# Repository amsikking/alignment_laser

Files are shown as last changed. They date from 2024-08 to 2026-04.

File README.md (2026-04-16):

# alignment_laser



How to build a simple alignment laser for typical optical alignment tasks.

## Overview:
This alignment laser is fast and simple to build, and easy to move around the lab. It can be used for most alignment tasks, from simple arrangements (e.g. placing a few mirrors) to complex systems (e.g. building sophisticated microscopes).

**Note:** It is not essential to copy this exact design, the key features and methods shown here can be applied to other setups.

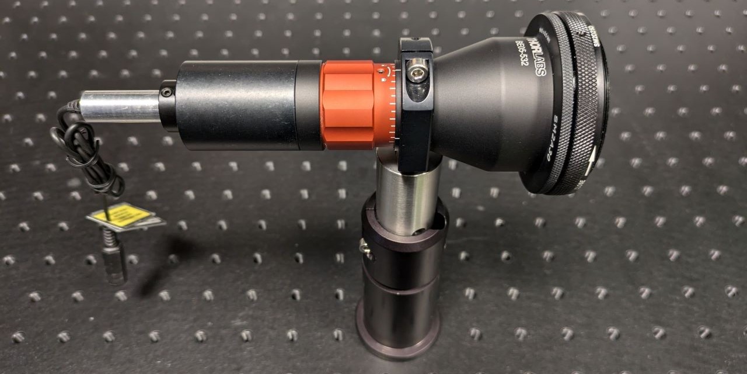
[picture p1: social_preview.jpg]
social_preview


## Features:
- **A 532nm laser diode:** this sits in the middle of the visible spectrum (~380-750nm), and is good for aligning to the central wavelength of typical achromatic lenses. Also, the human eye is sensitive to the bright green color which helps during alignment.
- **A round ~3.5mm diameter beam profile:** elliptical or otherwise asymmetric beams are difficult to work with, a round beam is usually best.
- **A power of 4.5mW:** bright enough for most tasks, but not excessive.
- **A 5x beam expander with collimation adjustment:** this gives a ~17.5mm diameter beam which is enough for most 1 inch optical alignment tasks (and exceeds most objective back focal plane diameters).
- **A variable iris:** this allows easy beam diameter adjustment in the range of ~1-17.5mm. Small diameter beams (e.g. 1mm) are good for checking back reflections and beam deviations from lenses or other optics. Large diameter beams (e.g. >5mm) are good for checking collimation and have a long propagation distance.
- **Balanced mechanics:** the assembly is easy to move around and bolt down in different positions. When paired with 2 adjustable mirrors, the alignment laser is fast to deploy in most situations.

## Build:
Go to the [cad](https://github.com/amsikking/alignment_laser/tree/main/cad) folder and open [alignment_laser_v1.0.pdf](https://github.com/amsikking/alignment_laser/blob/main/cad/alignment_laser_v1.0.PDF)
- Get the parts and screw them together (see the other CAD files for details).

## Test:
Download the repository, go to the [photos](https://github.com/amsikking/alignment_laser/tree/main/photos) folder and follow the numbered photos:

0) [**Check parts:**](https://github.com/amsikking/alignment_laser/blob/main/photos/0_all_parts_used.jpg) to follow exactly you’ll need these extra parts from Thorlabs:
    - Absorptive ND filter wheel (or filter set) for beam attenuation: NDC-100S-4M or NEK01 (or both).
    - A camera for looking at the beam profile: e.g. CS165MU1/M
    - Some shear plates for checking collimation: SI100 (5-10mm beams), SI050P (2.5-5mm beam plate) and SI254P (10-25.4mm beam plate).
    - **Note:** If you don’t have these parts, you can do something similar with other tricks (e.g. alternative beam attenuation and profiling methods, and checking collimation with distance).
1) [**Check laser collimation:**](https://github.com/amsikking/alignment_laser/blob/main/photos/1_check_laser_collimation.jpg) attenuate the beam and use the 2.5-5mm shear plate to check the laser output is collimated.
2) [**Optional -> measure beam profile:**](https://github.com/amsikking/alignment_laser/blob/main/photos/2_measure_laser_beam_profile.jpg) use a camera and compare the measured beam profile to the specification. Attenuate with ND filters on the camera and use the back reflection to align. See the [beam_profile_example](https://github.com/amsikking/alignment_laser/tree/main/beam_profile_example) folder and the [gaussian_beam_profiler](https://github.com/amsikking/gaussian_beam_profiler) repository for more.
3) [**Add target:**](https://github.com/amsikking/alignment_laser/blob/main/photos/3_align_target_to_laser.jpg) use an alignment card (or similar) and center the beam on a target.
4) [**Add 5x beam expander:**](https://github.com/amsikking/alignment_laser/blob/main/photos/4_add_collimator_and_iris.jpg) the large beam (iris open) should have a nice smooth profile over ~17.5mm.
5) [**Check beam deviation:**](https://github.com/amsikking/alignment_laser/blob/main/photos/5_close_iris_and_check_beam_deviation.jpg) with a small ~1mm beam (iris closed), check the position of the beam on the target. A small deviation of a few mm is normal after adding the beam expander since we are relying on the mechanical alignment of the parts.
6) [**Add large shear plate:**](https://github.com/amsikking/alignment_laser/blob/main/photos/6_add_large_shear_plate.jpg) With a small ~1mm beam, add the 10-25.4mm shear plate and use the double reflections to align the plate with the line on the frosted screen.
7) [**Check collimation:**](https://github.com/amsikking/alignment_laser/blob/main/photos/7_check_collimation_with_large_shear_plate.jpg) Open the iris to ~17.5mm and check the collimation with the shear plate.
8) [**Adjust collimation:**](https://github.com/amsikking/alignment_laser/blob/main/photos/8_adjust_collimation_with_large_shear_plate.jpg) use the beam expander adjuster to set the collimation with the shear plate.
9) [**Re-check collimation:**](https://github.com/amsikking/alignment_laser/blob/main/photos/9_check_collimation_with_medium_shear_plate.jpg) use the 5-10mm shear plate to double check collimation, then fix the position of the beam expander adjuster with the set screw.

If the testing goes smoothly, the portable alignment laser is now ready to use!

## Acknowledgments:
Inspired by, and with contributions from: [jlazzaridean](https://github.com/jlazzaridean), [fadero](https://github.com/fadero) and [AndrewGYork](https://github.com/AndrewGYork).

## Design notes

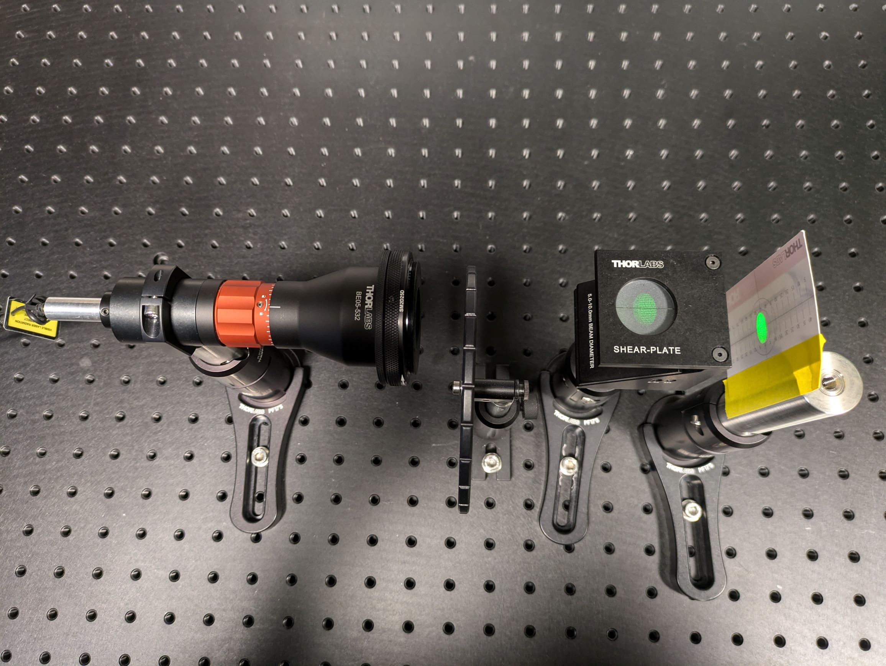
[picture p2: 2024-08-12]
photos/9_check_collimation_with_medium_shear_plate.jpg

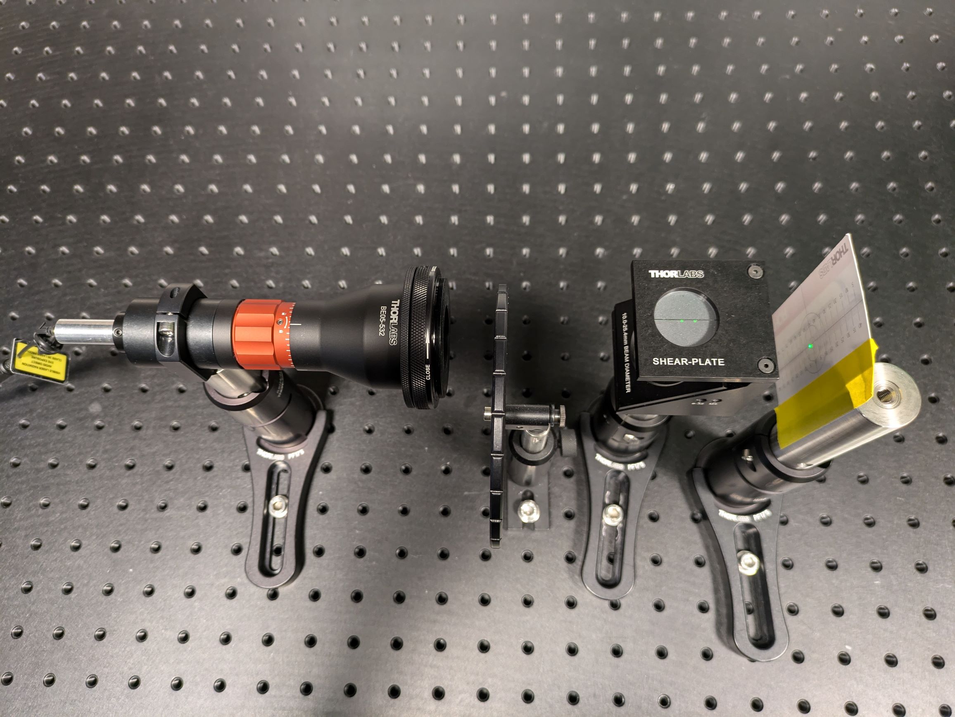
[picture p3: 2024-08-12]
photos/6_add_large_shear_plate.jpg

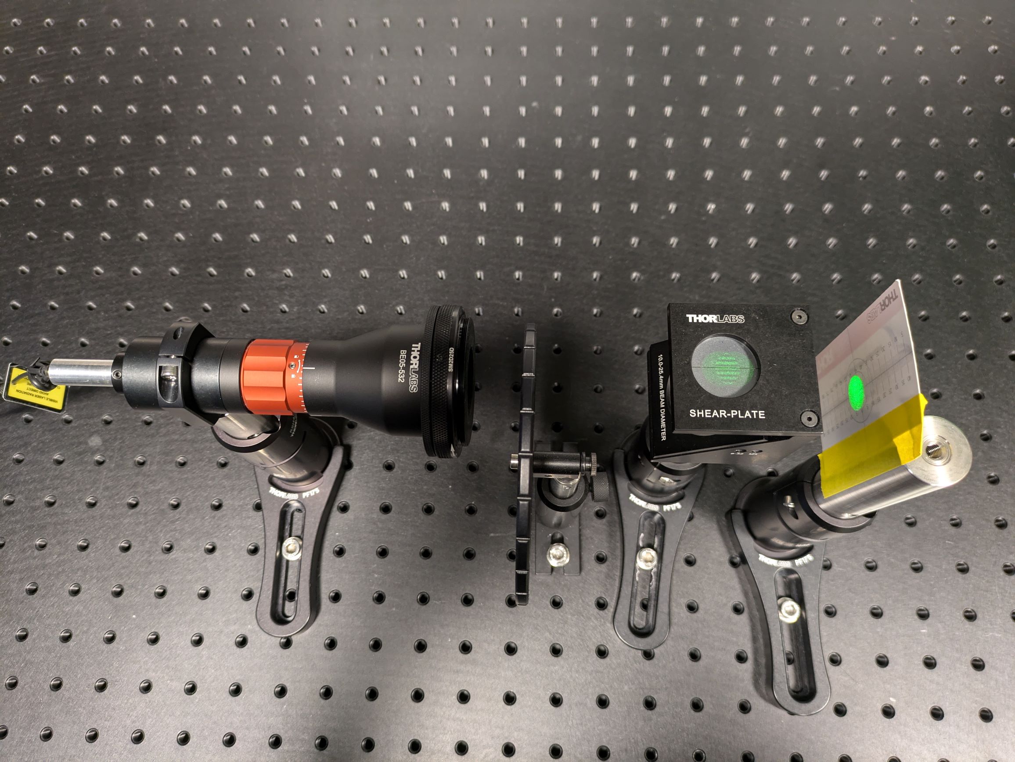
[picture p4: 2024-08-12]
photos/8_adjust_collimation_with_large_shear_plate.jpg

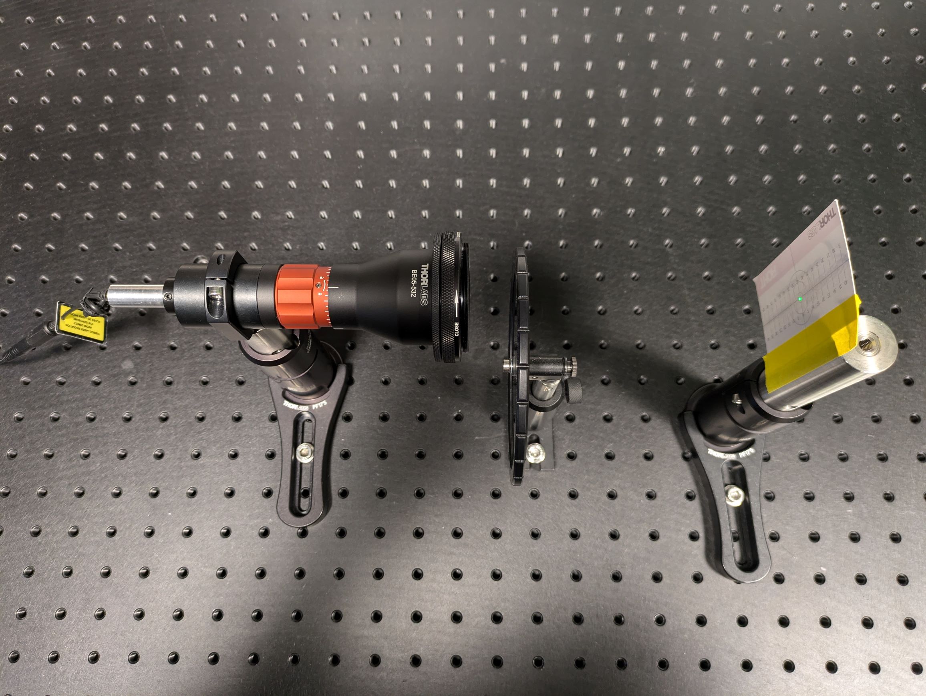
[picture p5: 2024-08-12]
photos/5_close_iris_and_check_beam_deviation.jpg

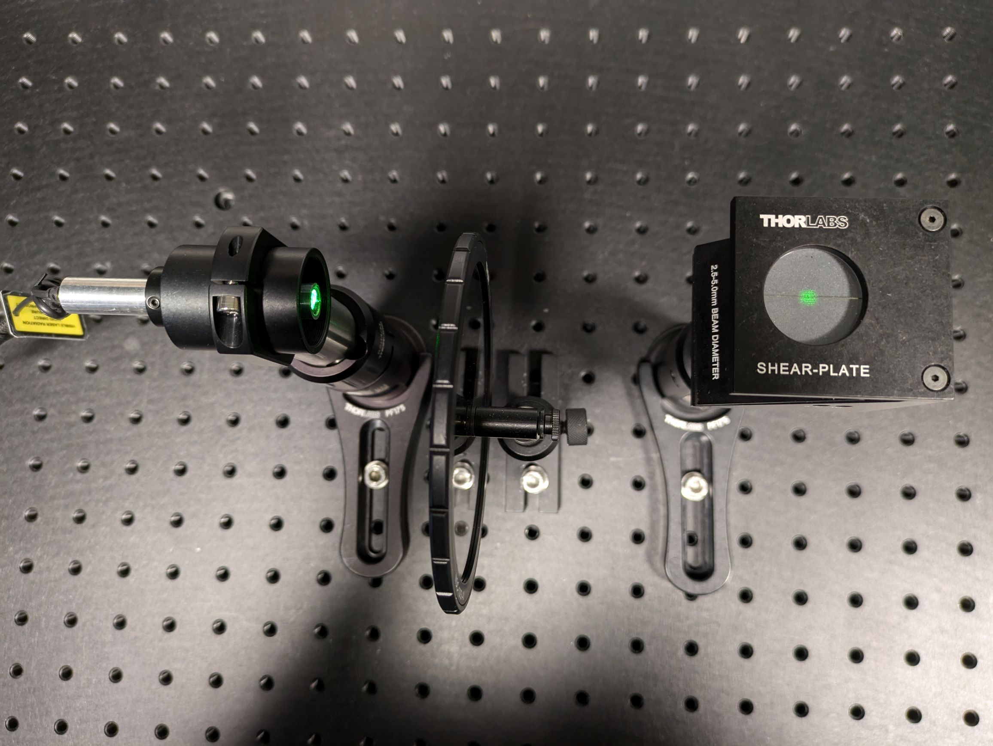
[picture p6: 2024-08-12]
photos/1_check_laser_collimation.jpg

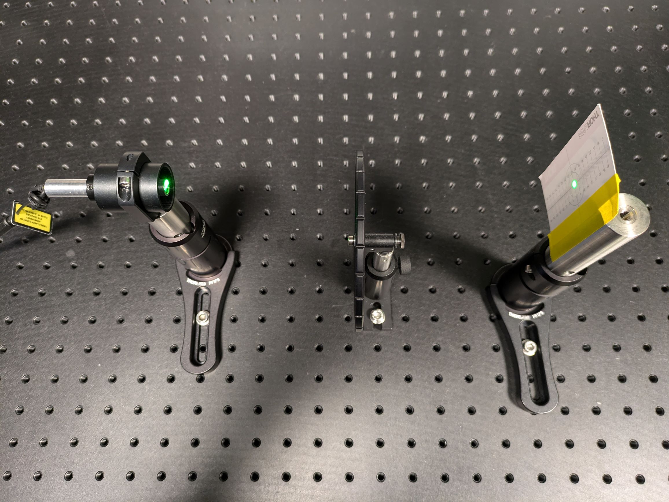
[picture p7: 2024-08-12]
photos/3_align_target_to_laser.jpg

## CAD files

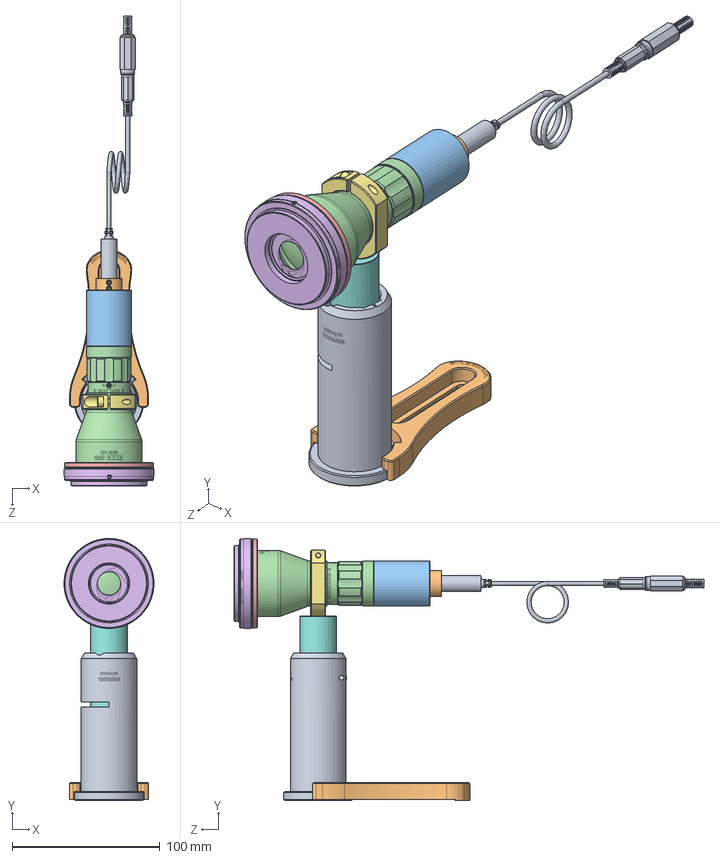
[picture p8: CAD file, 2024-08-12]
cad/alignment_laser_v1.0.SLDASM
61.0 x 177.6 x 318.3 mm
CPS532-Solidworks
AD11F-Solidworks
SM1M15-Solidworks
BE05-532-Solidworks
SM2A30-Solidworks
SM2D25D-Solidworks
SM1RC_M-Solidworks
RS100_M-Solidworks
RSH4_M-Solidworks
PF175B-Solidworks

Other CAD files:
cad/alignment_laser_v1.0.SLDDRW

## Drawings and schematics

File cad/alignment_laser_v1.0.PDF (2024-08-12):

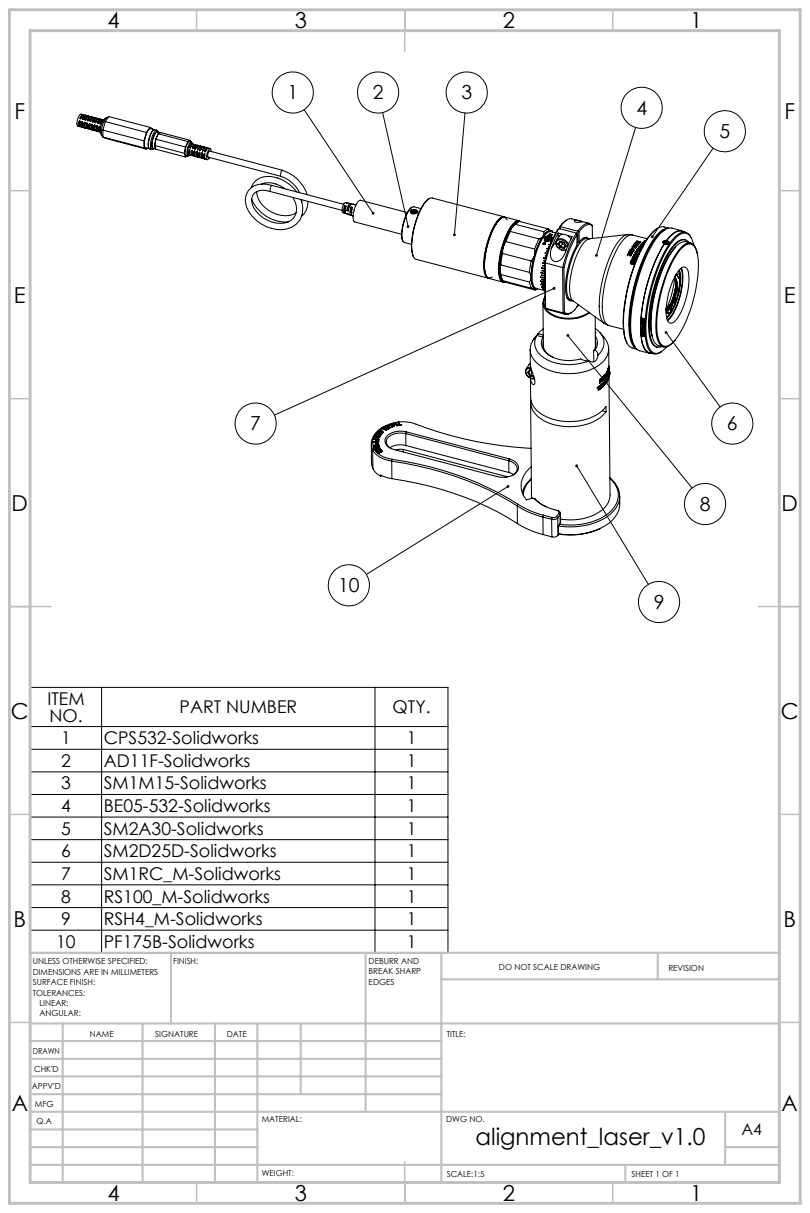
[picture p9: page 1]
SCALE:1:5; SHEET 1 OF 1

ITEM NO. | PART NUMBER | QTY.
1 | CPS532-Solidworks | 1
2 | AD11F-Solidworks | 1
3 | SM1M15-Solidworks | 1
4 | BE05-532-Solidworks | 1
6 | SM2D25D-Solidworks | 1
7 | SM1RC_M-Solidworks | 1
8 | RS100_M-Solidworks | 1
9 | RSH4_M-Solidworks | 1
10 | PF175B-Solidworks | 1

UNLESS OTHERWISE SPECIFIED: DIMENSIONS ARE IN MILLIMETERS SURFACE FINISH: TOLERANCES: LINEAR: ANGULAR: | FINISH: | DEBURR AND BREAK SHARP EDGES | DO NOT SCALE DRAWING | REVISION

NAME | SIGNATURE | DATE | | | | TITLE:

DRAWN
CHK'D
APPV'D
MFG
Q.A | | | | MATERIAL: | DWG NO. alignment_laser_v1.0 | A4
